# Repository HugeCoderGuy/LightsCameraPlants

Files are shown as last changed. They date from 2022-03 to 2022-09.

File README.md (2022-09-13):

# LightsCameraPlants
### Automated Phenotyping hardware/software to assist with real-time data collection and analysis for under $120[^1].
[^1]: The price is roughly $110 if you already own a monitor, keyboard, mouse, hdmi, usb cords and have access to a 3d printer and soldering iron. Otherwise all of the extra gizmoes and gadgets bring the price up to roughly $230.

<p align="center">

</p>

## Summary:
Included are all of the necessary files to complete automated measurements of leaf area for plants grown on 100mmx15mm square petri-dishes. Measurements of the plants are taken in a standardized 3D-printed enclosure that eliminates common issues such as glare, camera positioning, and image cropping for image analysis. This alleviates much of the post-processing required with other automated phenotyping methods and allows the user to identify leaf area measurements in real-time. Users that are disinterested in leaf area can still utilize this system for streamlined image collection and image/data transfer to Google Drive[^2]. 
[^2]: Included in the files_to_print folder is a tray to hold your classic petri dish

## Table of Contents
2. [ Components ](#parts)
3. [ Setup ](#setup)
4. [ User Guide ](#guide)
5. [ Acknowledgements ](#ak)

## Components:
<p align="right" alt="side Text">
<strong>Prototype used to test lighting orientation in housing</strong>
</p>
side Image

- [Raspberry pi 3b, 4, or 400](https://www.adafruit.com/product/4296)
- [NeoPixel Diffused 8mm Through-Hole LED - 5 Pack](https://www.adafruit.com/product/1734?gclid=EAIaIQobChMI-vbjzefJ9gIV1BatBh1jzA-aEAAYASAAEgI8xfD_BwE) 
- [7" Touchscreen](https://www.adafruit.com/product/2407)
- [HDMI cord](https://www.adafruit.com/product/2197)
- [USB Cord & Power Supply](https://www.adafruit.com/product/1995)
- [USB to micro usb adapter](https://www.adafruit.com/product/2185)
- [SD Card](https://www.adafruit.com/product/2820)
- [Raspberry Pi Camera V2](https://www.raspberrypi.com/products/camera-module-v2/)
- [Heat-set inserts](https://www.adafruit.com/product/4256)
- [M3 Screws](https://www.amazon.com/Sutemribor-320Pcs-Stainless-Button-Assortment/dp/B07CYNKLT2/ref=sr_1_4?keywords=m3+screws&qid=1647405731&sr=8-4)
- [Keyboard and mouse if you want it](https://www.adafruit.com/product/1738)
- 3D Printer Filament (roughly 350g)
- [100mmx15mm Square Petri Dish](https://www.simport.com/en/products/54-d210-16-square-petri-dish-with-grid.html)

<p align="right" alt="side Text">
<strong>Various Prototype Housing Designs</strong>
</p>
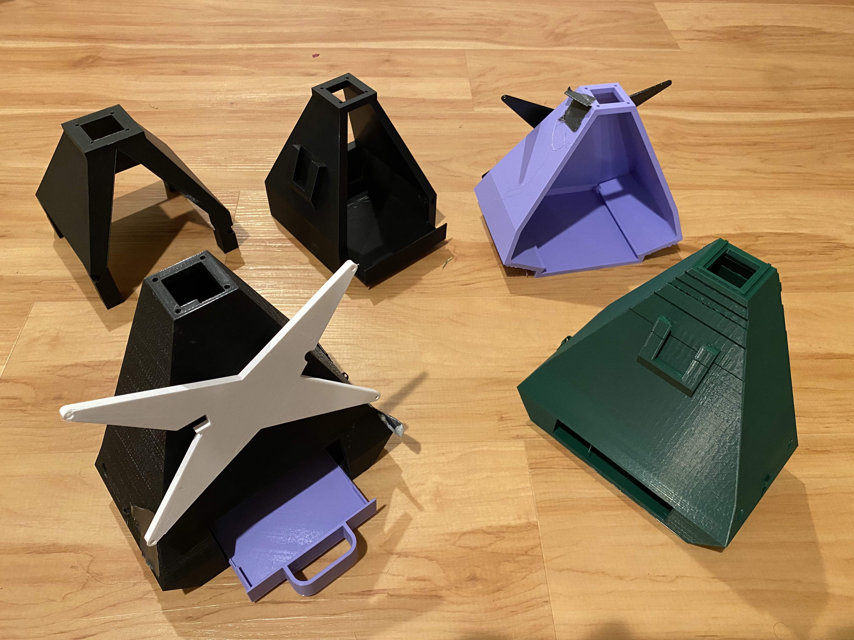
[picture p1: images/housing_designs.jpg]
side Image


**Tools**
- A 3D printer
- Soldering tools and setup
- [Heat-set insert tip](https://www.adafruit.com/product/4239_)
<br>

## Setup
### Part 1: Hardware
1. Download the raspberry pi case .stl files[^3], housing.stl, tray.stl, and screen_backing.stl files from the files_to_print folder. Use [Cura](https://ultimaker.com/software/ultimaker-cura) to develop a gcode file for your 3D prints of the components. I recommend that you use these settings:
   - 20% infill (I generally use triangles)
   - Normal - .15mm profile for all prints
   - adhesion if printing the display backing or raspberry pi case
   - Matte Black PLA filament for the 3D printer
   - Supports (overhang angle = 80)
2. Sand down the edges of the plant tray so that they are smooth. Slide the tray into the enclosure to ensure that the edges have been smoothed enough.
3. Using the heat-set insert tip with a soldering iron heated to 700F, press heat inserts into the four holes on the back of the enclosure and four holes on the display backing. 
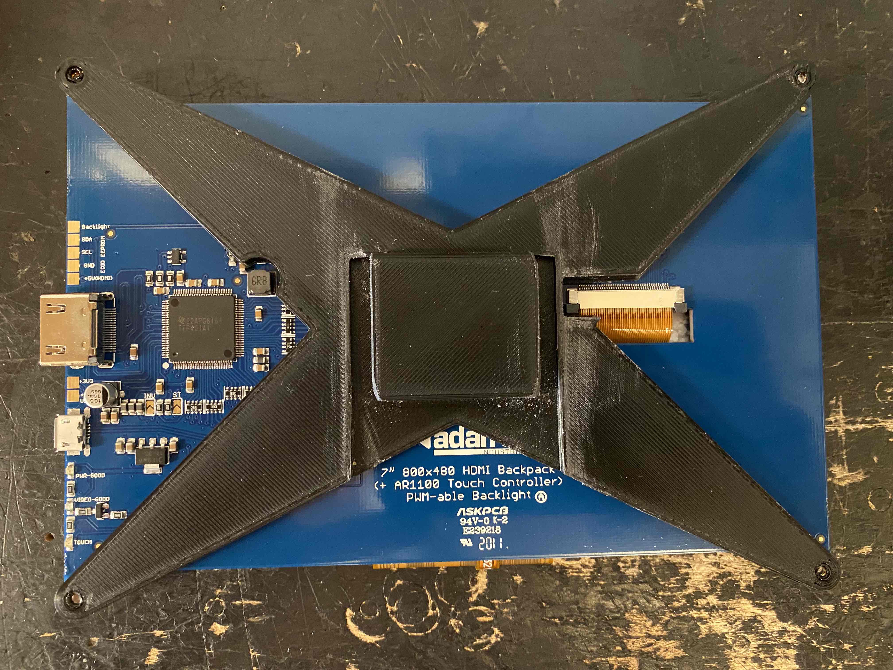
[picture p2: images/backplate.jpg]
side Image


4. Attach the touchscreen to the display backing using x4 M3x8mm screws
5. slide the display backing into the enclosure slot. Sandpaper down the interfaces if the connection is rough.
6. Connect the pi camera through the lid of the raspberry pi case. Then seal the case with x4 M3x16mm screws. They should screw right into the plastic.
7. Screw the raspberry pi and its case onto the back of the enclosure into the x4 inserts using x4 M3x8mm
8. Slide the backplate onto the main housing and ensure that the touchscreen has a snug fit with the backplate
9. Slide a piece of paper with letters into the tray position. Using the white ring that comes with the picamera, adjust the focus of the picamera until the image is roughly sharp enough to read the letters.
10. Slide the picam into the slot at the top of the enclosure so that the top of the camera is flush with the slot. Then use electrical tape to hold the camera in place. WARNING: Do not use any other tape other than electrical tape. The camera is incredibly sensitive to static electricity and will break if scotch tape is applied to the back of the camera.
11. solder neopixels together in a chain with 3 wires that have pin connectors for data, voltage, and ground. Be mindful of how long the wires are between each neopixel to ensure that they reach each of the holes. Refer to the image below for what each prong of the neopixel is used for
12. Connect the ground cable to the ground pin, the Vin cable to the 5V pin, and the data in line to GPIO21. Please refer to [online documentation](https:includelineheree) for the specific pinout of your raspberry pi model. An example pinout of the pi3b is shown below with arrows referring to the correct pins.

<p align="center">
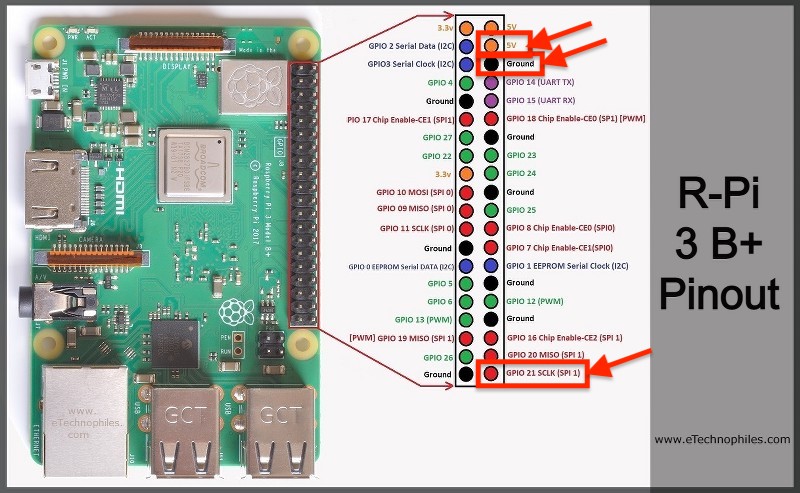
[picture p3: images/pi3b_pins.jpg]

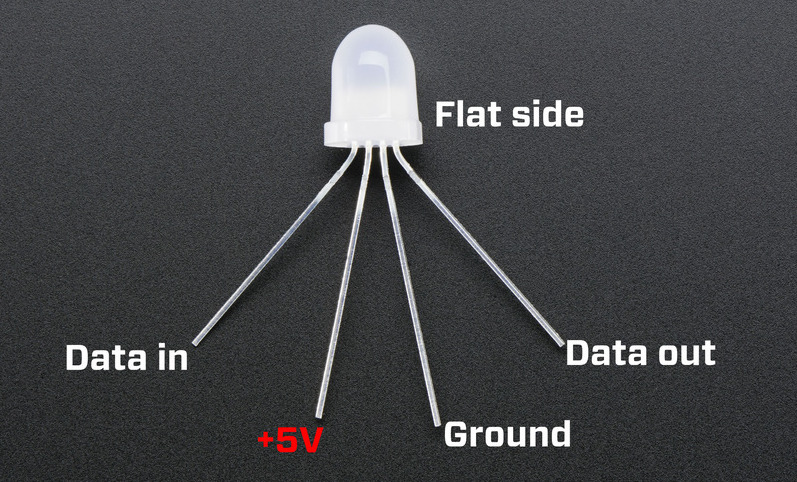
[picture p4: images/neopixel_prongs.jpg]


</p>

[^3]: Credits for the raspberry pi case file can be given to [0110-M-P on Thingiverse](https://www.thingiverse.com/thing:922740/files)

### Part 2: Software
1. Download the [Raspberry Pi Imager software](https://www.raspberrypi.com/software/) and set up the pi os on the fresh SD card. Refer to this [video](https://www.youtube.com/watch?v=ntaXWS8Lk34) for additional help setting up the sd card.
2. Place the sd card into the pi and then power it up with the micro usb. Plug the usb to micro usb cable and HDMI into the pi to connect it to the touchscreen display. Keyboard (if not using the pi 400) to the pi to interact with it.
3. Connect your pi to wifi. Without wifi you will not be able to operate the software or download the system dependencies. 
3. in the terminal, run `sudo raspi-config`, then click Interface Options followed by Legacy Camera. Finally, enable the camera and then click finish. You will likely have to reboot the pi. Note that if you are using a pi 3b, enabling the legacy camera will likely reduce the usable screen size on the 7" display due to the new driver for the pi 4.
4. Navigate to the terminal screen and enter
```
git clone https://github.com/HugeCoderGuy/LightsCameraPlants.git
```
4. Then enter
```
cd ~/LightsCameraPlants
bash setup1.sh
```
When prompted, type Y followed by enter to continue throughout the installation. Make sure that you do not allow the pi to sleep while setup1.sh is running. If the pi sleeps or crashes, you can either try rerunning the script on reboot or re-flashing the SD card and trying again. The terminal may also prompt you to run `sudo dpkg --configure -a`. If so, do so and rerun the script or just `sudo python raspi-blinka.py` if the code got stuck on the blinka script. 
6. After the `setup1.sh` script runs, your pi should restart. Upon restarting, run this in the command line
```
cd ~/LightsCameraPlants
bash setup2.sh
```
7. Plug the usb camera into the pi and test that the software dependencies were installed correctly by running 
```
sudo python3 lightsandcamera.py -o /home/pi/Pictures -p 1
``` 
   Note that the directory in quotes after -o is the output directory. This folder is where images will be saved too and will be the folder that is synced with your google drive (refer to step 8 for google drive sync setup). Feel free to change this output directory to correspond to a folder with your current project.
   
8. **Setting up Google Drive Sync Functionality**
   1. LightsCameraPlants allows you to sync your output directory with a google drive folder to allow for easy documentation of samples. To do this you must first get authentication for Google Service API. Refer to [this PDF](https://d35mpxyw7m7k7g.cloudfront.net/bigdata_1/Get+Authentication+for+Google+Service+API+.pdf) for documentation on how to setup your authentication. 
   2. After downloading your credentials file. Copy and paste your client_id and client_secret without quotes into the `settings_to_be_edited.yaml` file in your LightsCameraPlants folder.
   3. Finally rename the `settings_to_be_edited.yaml` to `settings.yaml`. Make sure you do not accidentally share your client_id and client_secret.

## User Guide
1. After powering up the pi and plugging in all of the necessary hardware, navigate to the terminal and type
```
cd ~/LightsCameraPlants/
```
followed by
```
sudo python3 lightsandcamera.py -o /home/pi/Pictures -p 1
```
As stated previously, the /home/pi/Pictures call refers to the output directory that can be changed by creating a new folder, navigating to it in the terminal and then typing `pwd`, then copy/pasting that directory after the --output argument call.

**Other Arguments You can Call:**

*Airplane Mode*: To use the system in a location without wifi, at the cost of the google drive upload feature, you can put the system in airplane mode by calling
```
sudo python3 lightsandcamera.py -o /home/pi/Pictures --airplaneMode True
```
or 
```
sudo python3 lightsandcamera.py -o /home/pi/Pictures -a True
```
*Pi Camera*: If you want to use an usb camera rather than picamera, call
```
sudo python3 lightsandcamera.py -o /home/pi/Pictures
```
Note that you can call both of the --airplaneMode and --picamera args in the same statement.

2. Right-click the link that appears in the terminal after the "warming up camera..." statement and then click "Open URL". If you are just using the touchscreen, copy and paste the link into chromium
   - If you are currently unable to connect to wifi and do not need the drive features, recall that you can add the `-a True` argument to the script call which activates airplane mode
3. Sign into your appropriate google account and allow the api to access your drive

<p align="center">

</p>

4. Buttons and Functions
   - A: The LED Slider allows you to change the hue of the Neopixel lights. 0% is pure white light and 100% is pure green light. This functionality is meant to assist with the software's identification of leaf area if needed.
   - B: The Threshold slider defines how the software identifies the leaves. A lower threshold is more inclusive of potential leaf measurements while a higher threshold is exclusive. Note that minor changes in the threshold can have major effects on leaf identification errors.
   - C: "Measure Leaf Area" button takes the current image from the live feed and processes the image to find leaf area. The final displayed image on the right shows the regions of identified leaf area. If the leaf area is not identified, alter the threshold or LED hue to help the system recognize leaf area.
   - D: If the processed image on the right has appropriately identified the leaf area in the sample, click the "save image" button to save the original snapshot without the leaf outlines. The associated leaf area measurements will be stored in the "Data" folder in a .csv titled with the date of the measurements. The image and measurements will be saved to the output directory called in `sudo python3 lightsandcamera.py "-o INSERT_OUTPUT_DIRECTORY_HERE"`.
   - E: Once you are done collecting samples sync the output directory content with a Google Drive by inserting the drive ID into box E_1. The drive ID is the series of numbers at the end of the URL for that google drive folder. Then click the "sync output directory with Google Drive" button to automatically upload all of your data to the cloud.
    - For example, if your google drive folder has the url "https://drive.google.com/drive/u/0/folders/1M1Uz_Dlx6QlVlQfRi8ftzgViss0udwUW", copy and paste the last bit, 1M1Uz_Dlx6QlVlQfRi8ftzgViss0udwUW into the text box.
5. Closing the program can be done by clicking the x in the upper right corner or typing ctr+c once or twice into the terminal.

<br><br>
<strong>Acknowledgements</strong>

This project was done for and funded by the UC Davis Bloom Lab. Huge thanks go out to Arnold Bloom for accepting me into his lab, [Jordan Stefani](https://github.com/massivejords) for providing the code that assists with leaf area analysis, and [Anna Knapp](https://github.com/AnnaKnapp) for providing me with essential mentorship as I became familiar with the Raspberry Pi platform and its integration with the numerous python libraries.

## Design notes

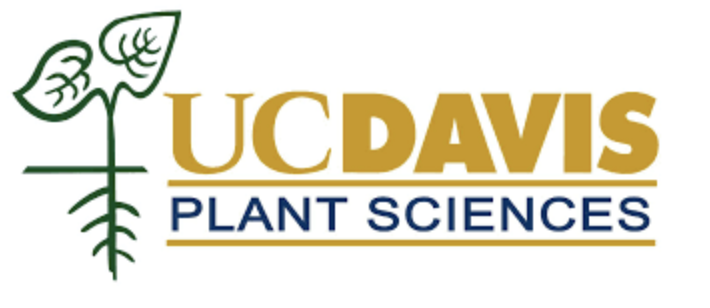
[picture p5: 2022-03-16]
startup_image.png

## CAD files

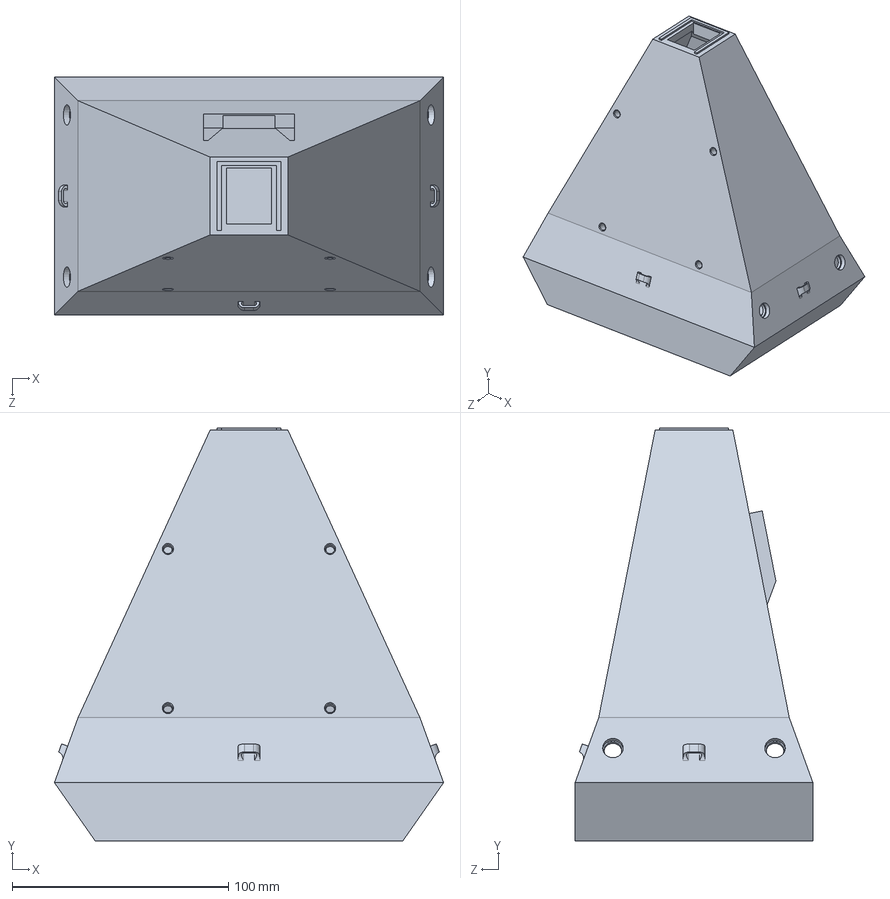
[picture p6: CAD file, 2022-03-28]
files_to_print/enclosure_pi_camera.SLDPRT
180.0 x 191.0 x 110.0 mm

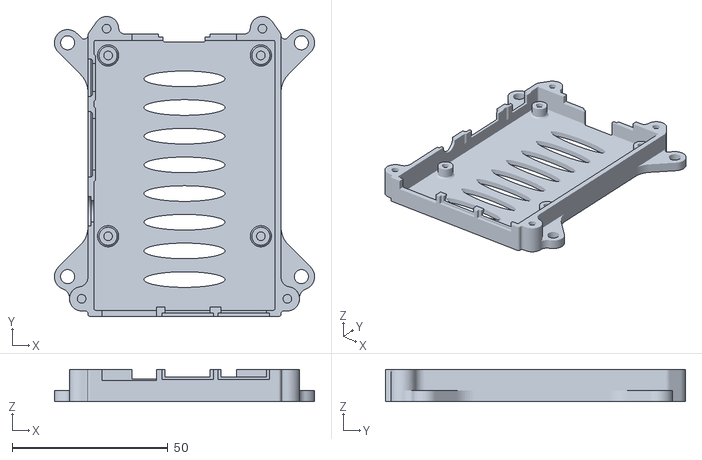
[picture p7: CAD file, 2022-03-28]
files_to_print/rpi3-bottom_netfabb.stl
83.5 x 96.2 x 10.3

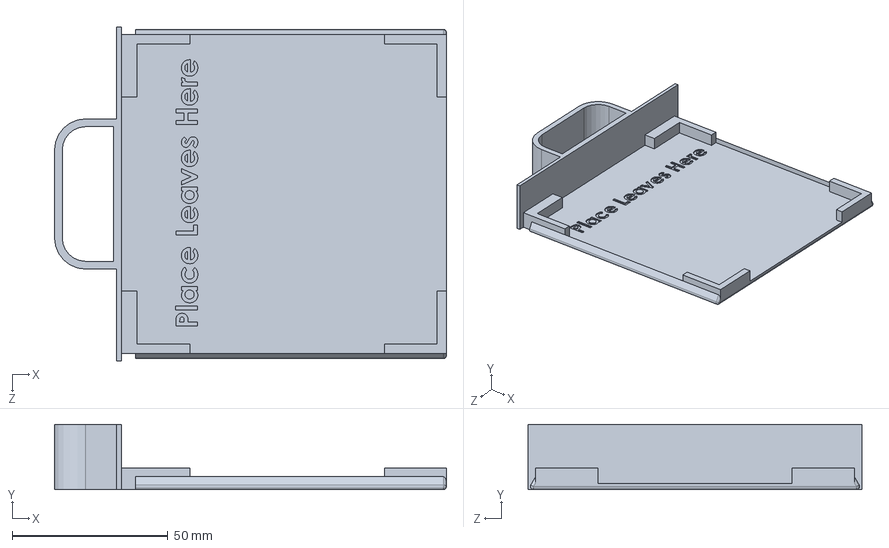
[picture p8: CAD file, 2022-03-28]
files_to_print/plant_tray.SLDPRT
126.0 x 21.0 x 107.3 mm

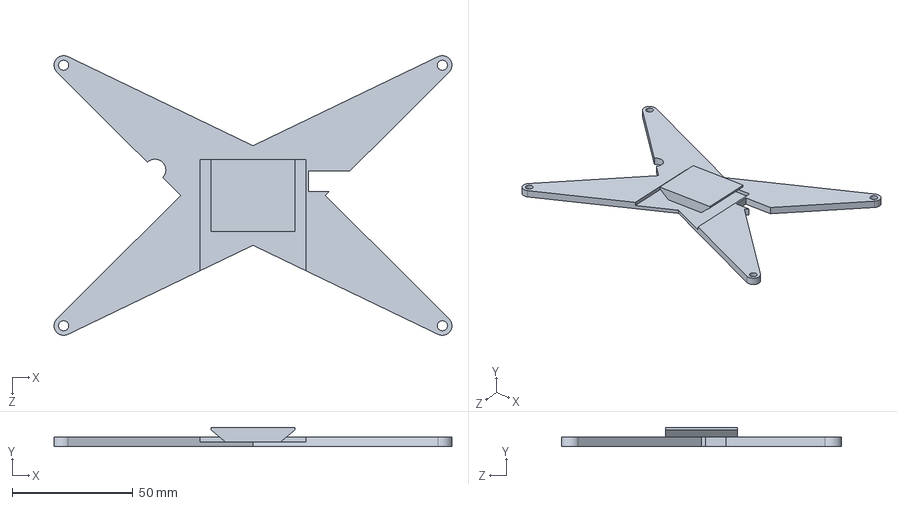
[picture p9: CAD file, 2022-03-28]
files_to_print/display_backing.SLDPRT
165.0 x 8.00 x 116.0 mm

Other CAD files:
files_to_print/display_backing.STL
files_to_print/enclosure_pi_camera.STL
files_to_print/plant_tray.STL

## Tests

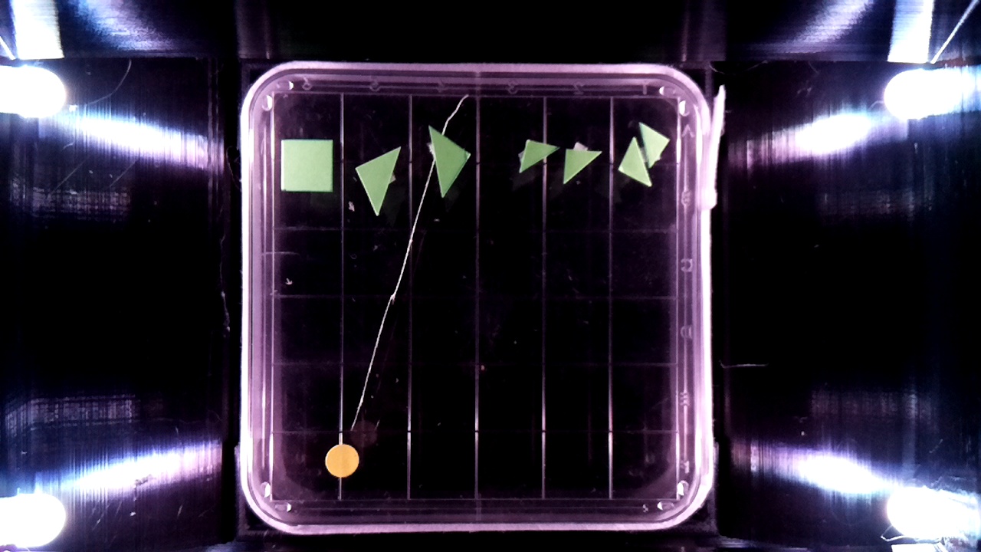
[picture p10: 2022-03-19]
ELA_Test.jpg

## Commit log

2021-10-27 Camera and light control script
2022-01-30 "Adding rough drafts of setups files for new raspberry pi setup"
2022-03-28 "including CAD files for enclosure"
    [display_backing.SLDPRT, display_backing.STL, enclosure_pi_camera.SLDPRT, enclosure_pi_camera.STL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]
